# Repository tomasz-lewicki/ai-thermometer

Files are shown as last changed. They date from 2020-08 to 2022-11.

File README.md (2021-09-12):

# AI Thermometer
Contactless temperature mesurement using IR & RGB cameras and Deep CNN facial detection.

### Normal temperature

### Elevated temperature


## What's new in v0.4
* New facial detector (handles partial occlusion, e.g. with a mask)
* Added IR camera drift compensation with an external blackbody

## Hardware 
To build this project you will need:
|#|Part|link|Price (USD)|
|-|-|-|-|
|1|Jetson Nano Dev Kit|[link](https://www.sparkfun.com/products/16271)| 99 | 
|3|FLIR Lepton 3.5 IR Camera | [link](https://store.groupgets.com/products/flir-lepton-3-5)| 199 |
|4|GroupGets Purethermal2 Module | [link](https://store.groupgets.com/products/purethermal-2)| 99 |
|2|Raspberry Pi Camera Module V2.1 |[link](https://www.sparkfun.com/products/14028) | 25 |
|5|Noctua cooling fan | [link](https://www.amazon.com/Noctua-NF-A4x10-PWM-4-Pin-Premium/dp/B07DXRNYNX/) | 14 |
|6|3D printed enclosure | [https://a360.co/3nmDML3](https://a360.co/3nmDML3) | - |
|total | | | 436 |

Enclosure (live model available from [https://a360.co/3nmDML3](https://a360.co/3nmDML3) ): 
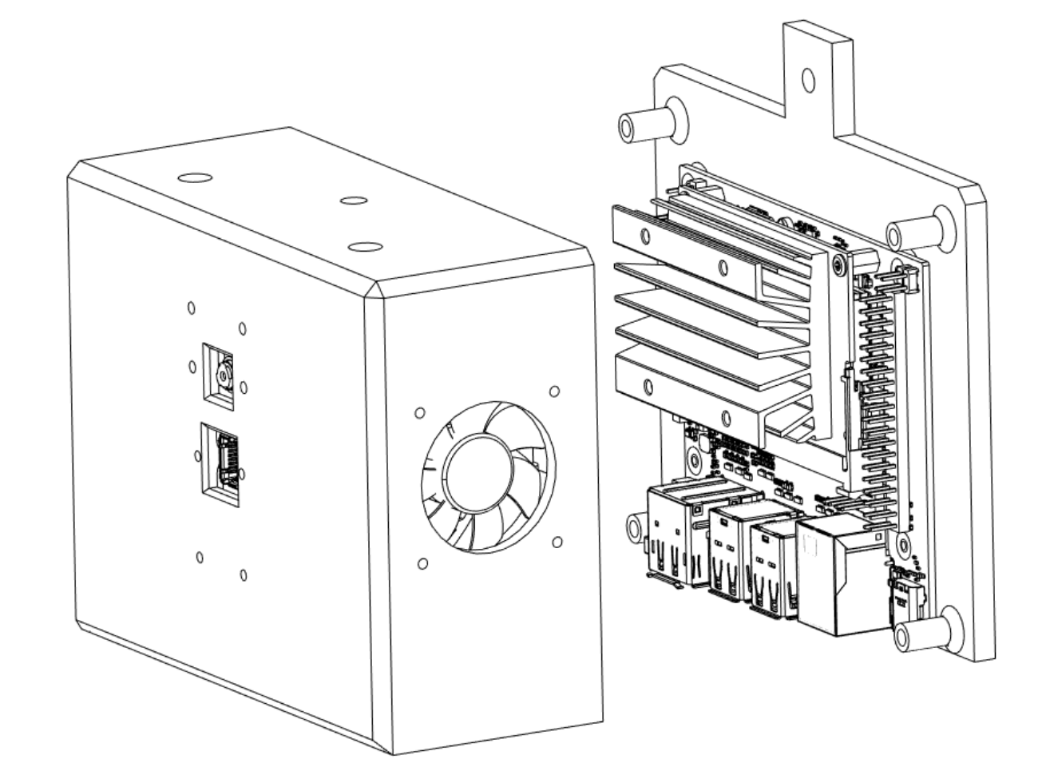
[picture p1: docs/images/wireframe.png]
wireframe image


## Quickstart 

1. Flash Nvidia Jetson Nano with the latest Nvidia JetPack. Update package manager

```shell
sudo apt update && sudo apt upgrade
```

2. Build OpenCV >4.4. It is required for CUDA DNN support.
```shell
wget https://raw.githubusercontent.com/mdegans/nano_build_opencv/master/build_opencv.sh
chmod +x build_opencv.sh
./build_opencv.sh
```
3. Build pytorch (instructions [here](https://forums.developer.nvidia.com/t/pytorch-for-jetson-version-1-7-0-now-available/72048))

4. Download AI Thermometer

```shell
git clone --recursive https://github.com/tomek-l/ai-thermometer
cd ai-thermometer
```

5. Run AI Thermometer

```shell
python3 main.py
```

6. Optionally, 3D print & assemble the enclosure from [https://a360.co/3nmDML3](https://a360.co/3nmDML3)

## Limitations

### IR and RGB camera alignment.

The current way of calculating the correspondence between IR and RGB cameras is not ideal.
Factors, such as the non-rigid mount of the sensor on the Raspberry Pi CMV2.1 don't help.
I'm actively working on calibration code that takes into account the intrinsic parameters of both cameras, which should allow for obtaining a pixel-level correspondence between the imags.

## FAQ/common issues:

1. `uvc_open error -3`

Reason: Your current user does not have r/w access to the PureThermal USB device. 

For a quick and dirty fix you can do do:
```shell
echo 'SUBSYSTEM=="usb",  ENV{DEVTYPE}=="usb_device", GROUP="plugdev", MODE="0664"' | sudo tee /etc/udev/rules.d/10-libuvc.rules 
sudo udevadm trigger
```
(this gives camera access to all users)

For a better, fine-grained permission setup, create a new group, give permissions to that group only and your user to the newly created group. You can read more [here](http://wiki.ros.org/libuvc_camera#Permissions).

2. `Illegal instruction (core dumped)`

Reason: The provided  ```libuvc.so``` is compiled for AArch64.
It is a custom version of libuvc that supports Y16 video format. If you're using different architecture, you will need to build the library from source:

```shell
git clone https://github.com/groupgets/libuvc
cd libuvc
mkdir build
cd build
cmake ..
make
cp libuvc.so ~/ai-thermometer/ir/libuvc_wrapper
```

3. using sudo or getting `permission denied`

You don't need ```sudo``` to run the code in this repository 🙂

## Previous versions

## Version 0.2: Haar Cascade + FLIR Lepton 3.5 temp. measurement (~10FPS, CPU only)
Watch full video: [https://www.youtube.com/watch?v=j9eo9Cs8J8I](https://www.youtube.com/watch?v=j9eo9Cs8J8I)

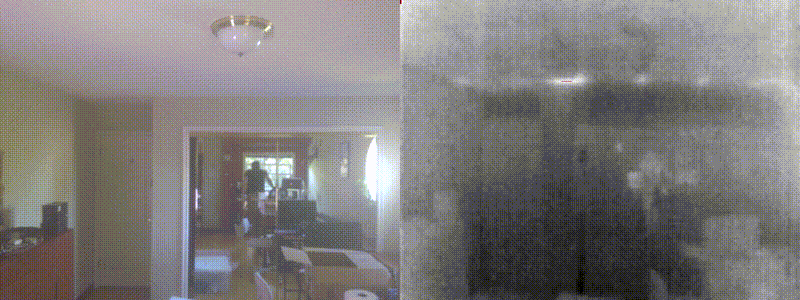
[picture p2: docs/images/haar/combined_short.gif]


## Version 0.1: SSD (COCO) + FLIR Lepton 3.5 temp. measurement (~12FPS w/ GPU accel.)
Watch full video: [https://www.youtube.com/watch?v=i2XMtshdjn8](https://www.youtube.com/watch?v=i2XMtshdjn8)



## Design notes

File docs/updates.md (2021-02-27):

# Hardware V2 update

## Camera Upgrade
The RGB camera module has been upgraded from the `Raspberry Pi CM V2.1` to a `Sainsmart IMX219`. 

The main reason for that change is the ridgidity of the assembly.
Specifically, the sensor on the CM V2.1 is held in place on the PCB with a piece of double-sided adhesive.
Even a sub-milimeter shift to the camera position can tilt the camera plane by a few degrees, and mess up the calibration.
That's bad for any machine-vision application.

In the Sainsmart camera module, the sensor is soldered to the PCB, and the plastic lens assembly is screwed down to the board. This is a much more ridgid assembly, making the RGB-IR alignment more robust.

## Antennas

# Software Update
- Support multiple detectors (SSD, retinaface)

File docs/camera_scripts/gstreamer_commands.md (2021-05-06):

# IR + RGB display simultaneously
```
gst-launch-1.0 nvarguscamerasrc sensor_mode=0 ! 'video/x-raw(memory:NVMM),width=3264, height=2464, framerate=21/1, format=NV12' ! nvvidconv flip-method=2 ! 'video/x-raw,width=800, height=600' ! videoconvert ! ximagesink & gst-launch-1.0 v4l2src device=/dev/video1 ! video/x-raw,format=UYVY ! videoscale ! video/x-raw,width=800,height=600 ! videoconvert ! ximagesink
```

# RGB

## Capture at full resolution, display on the screen
```shell
gst-launch-1.0 nvarguscamerasrc sensor_id=0 ! 'video/x-raw(memory:NVMM),width=3264, height=2464, framerate=21/1, format=NV12' ! nvvidconv flip-method=2 ! 'video/x-raw,width=960, height=720' ! nvvidconv ! nvegltransform ! nveglglessink -e
```

## Cropped
```shell
gst-launch-1.0 nvarguscamerasrc sensor_id=0 ! 'video/x-raw(memory:NVMM),width=3264, height=2464, framerate=21/1, format=NV12' ! nvvidconv flip-method=2 ! videocrop top=96 left=137 right=137 bottom=96 ! 'video/x-raw,width=800, height=600' ! nvvidconv ! nvegltransform ! nveglglessink -e
```

## General form to add cropping:
```
gst-launch-1.0 -v videotestsrc ! videocrop top=96 left=160 right=160 bottom=96 ! ximagesink
```

## Nvidia overlay display
```
gst-launch-1.0 nvarguscamerasrc sensor_mode=0 ! 'video/x-raw(memory:NVMM),width=3264, height=2464, framerate=21/1, format=NV12' ! nvvidconv flip-method=2  ! nvvidconv top=100 bottom=2364 left=300 right=3164 ! 'video/x-raw(memory:NVMM),width=1440, height=1080' ! nvoverlaysink display-id=0 -e
```

## take away 137 on the sides, 

horizontal: 3264-137=3127
vertical: 2464-96=2368
```
gst-launch-1.0 nvarguscamerasrc sensor_mode=0 ! 'video/x-raw(memory:NVMM),width=3264, height=2464, framerate=21/1, format=NV12' ! nvvidconv flip-method=2  ! nvvidconv top=96 bottom=2368 left=137 right=3127 ! 'video/x-raw(memory:NVMM),width=1440, height=1080' ! omxh264enc ! qtmux ! filesink location=RGB.mp4 -e 
```

## Saving to files
Save 1080p (sensor sub-frame)
```shell
gst-launch-1.0 nvarguscamerasrc ! 'video/x-raw(memory:NVMM), width=1920, height=1080,format=NV12, framerate=30/1'  ! nvvidconv flip-method=2 ! omxh264enc ! qtmux ! filesink location=1080p_output_cropped.mp4 -e
```

Save 1080p (from full frame, then resize)
```shell
gst-launch-1.0 nvarguscamerasrc sensor_mode=0 ! 'video/x-raw(memory:NVMM),width=3264, height=2464, framerate=21/1, format=NV12' ! nvvidconv flip-method=2 ! 'video/x-raw,width=1440, height=1080' ! omxh264enc ! qtmux ! filesink location=1080p_from_full.mp4 -e
```

--------------------------------------------------------------------------------------------------------------------------------------------------------

# Capture from IR Lepton Camera

## IR camera display (w/ colormap)
```shell
gst-launch-1.0 v4l2src device=/dev/video1 ! video/x-raw,format=UYVY ! videoscale ! video/x-raw,width=800,height=600 ! videoconvert ! ximagesink
```

## IR camera display (RAW 16bit values)
```shell
gst-launch-1.0 v4l2src device=/dev/video1 ! video/x-raw,format=GRAY16_LE ! videoscale ! video/x-raw,width=800,height=600 ! videoconvert ! ximagesink
```

## IR  - Save 

### Colormap to jpeg
```
gst-launch-1.0 v4l2src device=/dev/video1 num-buffers=1 ! video/x-raw,format=UYVY ! videoscale ! video/x-raw,width=800,height=600 ! nvjpegenc ! filesink location=test_ir.jpg
```

### Gray 16-bit 160x120 to mp4
```shell
gst-launch-1.0 v4l2src device=/dev/video1 ! video/x-raw,format=GRAY16_LE ! videoscale ! video/x-raw,width=160,height=120 ! videoconvert ! omxh264enc ! qtmux ! filesink location=grayscale_raw.mp4 -e
```
## Save to avi
gst-launch-1.0 v4l2src device=/dev/video1 ! video/x-raw,format=GRAY16_LE ! videoscale ! video/x-raw,width=800,height=600 ! videoconvert ! jpegenc ! avimux ! filesink location=test.avi -e

## Gray 8-bit resized to 800x600
gst-launch-1.0 v4l2src device=/dev/video1 ! video/x-raw,format=GRAY8 ! videoscale ! video/x-raw,width=800,height=600 ! videoconvert ! omxh264enc ! qtmux ! filesink location=grayscale_raw.mp4 -e

To record footage from both IR and RGB cameras at the same time, do:
```shell
bash deploy_rgb.sh & bash deploy_ir.sh ; fg
```

To combine the footage, do:
```shell
bash combine_ir_rgb.sh
```

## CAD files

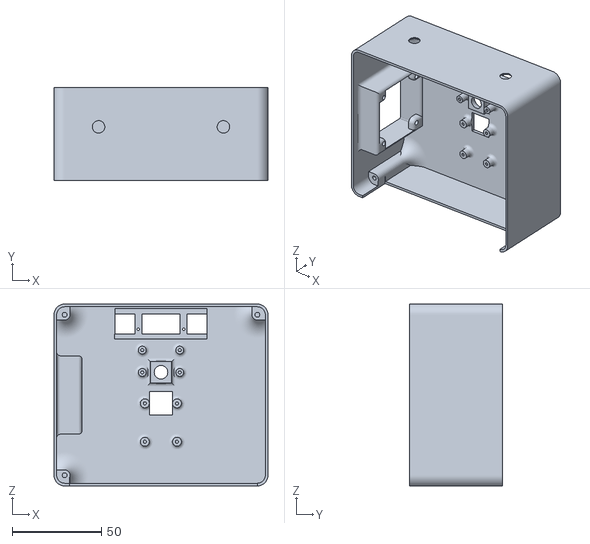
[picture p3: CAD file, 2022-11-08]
stl/top_shell.stl
120.0 x 52.0 x 102.0

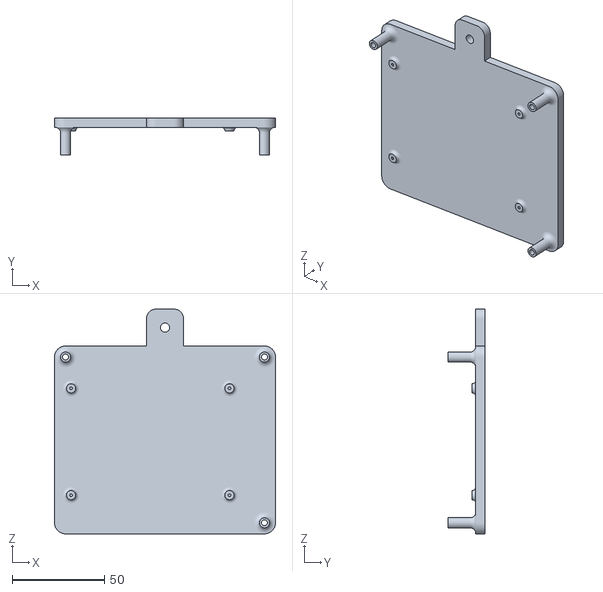
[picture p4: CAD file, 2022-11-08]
stl/base_plate.stl
120.0 x 20.0 x 122.0

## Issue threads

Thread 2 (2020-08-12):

tomasz-lewicki/ai-thermometer #2: where is requirements.txt

jazz-ai, 2020-08-12:
need requirements.txt

tomek-l, 2020-08-12:
Hi @jazz-ai !

The ```pip3 install -r requirements.txt``` was leftover from the previous AI Thermometer version that depended on ROS, as well as some other libraries. I will delete that line from the instructions.

Current version has no external requirements other than OpenCV 4.4  and nvidia Jetpack 4.4.

Let me know if you have any other issues.

jazz-ai, 2020-08-14:
I tried to run main.py
It is showing 
**uvc_open error -3**
and unable to start anything

tomek-l, 2020-08-16:
It means that your user doesn't have r/w access to the USB ports, so it cannot access the Pure Thermal device.

junartho, 2020-08-26:
hi @tomek-l 
nice codes. please tell me how to handle r/w access on usb ports.

tomek-l, 2020-08-26:
Hi @junartho 

If you want a quick and dirty solution do:
```shell
echo 'SUBSYSTEM=="usb",  ENV{DEVTYPE}=="usb_device", GROUP="plugdev", MODE="0664"' | sudo tee /etc/udev/rules.d/10-libuvc.rules 
sudo udevadm trigger
```
(this gives camera access to all users)

For a better, fine-grained permission setup, create a new group, give permissions to that group only and your user to the newly created group. You can read more [here](http://wiki.ros.org/libuvc_camera#Permissions).

tomek-l, 2020-08-26:
Let me know if that solved the problem :slightly_smiling_face:

junartho, 2020-08-26:
thank you for very fast response. 👍

closed 2020-08-26 by tomek-l

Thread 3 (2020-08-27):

tomasz-lewicki/ai-thermometer #3: Version 0.1: SSD (COCO) + FLIR Lepton 3.5 temp. measurement (~12FPS w/ GPU accel.)

junartho, 2020-08-27:
hi @tomek-l 

First of all, i wanna thank you for your codes. it really helps the communities at my place in this pandemic situation. however, these codes could only measure temperature with face straight to the camera and no mask used. i wonder if you have codes version 0.1 with SSD detection. I would appreciate it if you want to upload it.

tomek-l, 2020-08-28:
Hi @junartho ,

I didn't keep track of all the versions in parallel (v0.1, v0.2 and v0.3) but instead just overriding the repository with a newer version.  
You can view the v0.1 here: [https://github.com/tomek-l/ai-thermometer/tree/3bc78c2d7ce71a5f8fc7564c0c246c59196bae4e](https://github.com/tomek-l/ai-thermometer/tree/3bc78c2d7ce71a5f8fc7564c0c246c59196bae4e)

Keep in mind that the version 0.1:
1. Uses an SSD model, which is trained on the COCO dataset. While it gives you more classes (91 classes), it doesn't contain a "face" class, but rather a "person" class. This is less useful for the temperature estimation.

2. It uses ROS2 for communication. I dropped this approach in favour of communicating between threads. ROS2 is a bit of an overkill for this project, and folks might be unfamiliar with it. 

3. The setup is more involved, and the README is not as thorough.

I'm happy to help if you have any issues getting the v0.1 to work.

tomek-l, 2020-09-01:
Closing for now, but feel free to reopen if you have any further questions.

closed 2020-09-01 by tomek-l

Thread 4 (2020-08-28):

tomasz-lewicki/ai-thermometer #4: I am implementing ai thermometer with your kind explanation.

kos8108, 2020-08-28:
I am implementing ai thermometer with your kind explanation. 

Now I am building the environment of Raspberry pi camera v2 & lepton2.5 & PureThermal2.

But nothing has happened since Uvc_open error -3 appeared after python3 main.py. 

Can I know the solution? 

Of course, the individual operation of each sensor was confirmed.

thank you.

tomek-l, 2020-08-28:
Hi,

Did you change the permissions for the USB camera? (There's a short
explanation in readme.md)

kos8108, 2020-08-28:
Thank you so much.

It was executed with sudo without any problems.

Additionally, the temperature value of the ir sensor cannot be output, which part should I check?

Thank you always for your answer.

tomek-l, 2020-08-28:
Hey,

So if you wish to read the temperature value, you will need to add
something like this to the main loop:

print(ir_thread.frame.mean())

This will print the mean temperature of the 120x160 pixel array.

If you want to access the temperature of individual pixels, you'd do:

print(ir_thread.frame[0][0])

This way you'll access the value of the (0,0) pixel in degrees Celsius.

Hope this helps!

tomek-l, 2020-09-01:
Closing for now, but feel free to reopen if you have any further questions!

closed 2020-09-01 by tomek-l

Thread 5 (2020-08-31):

tomasz-lewicki/ai-thermometer #5: Couldn't get correct temperature

weshao, 2020-08-31:
Hi, I'm using Lepton 3.5 and purethermal 2, but my result temperature is around 100 (it should be close to 37,right?), and when I use the notebook(https://github.com/tomek-l/ai-thermometer/blob/master/docs/notebooks/Getting%20Started%20with%20Cameras.ipynb), the raw data for each pixel is around 8000 and after Kelvin to Celsius the result is around -195.
Do you have any idea about this?  Thanks.

tomek-l, 2020-08-31:
That's very weird. For me the raw values are (e.g. ~30315 for room at ~30deg C). The values being in 8000 range imply that the data is indeed in GRAY16_LE 16-bit format.

1. I presume that the following:
```shell
!gst-launch-1.0 v4l2src device=/dev/video1 ! video/x-raw,format=GRAY16_LE ! videoconvert ! ximagesink
```
gives you very dark (near black) image?

2. Could you send me an example png file from ```get_ir_image()``` so I can take a look?

You can use the following command to save a file:
```shell
!gst-launch-1.0 v4l2src device=/dev/video1 num-buffers=1 ! video/x-raw,format=GRAY16_LE ! videoconvert ! pngenc ! filesink location=/tmp/ir.png
```
It should be in ```/tmp/ir.png```

3. You are using jetson nano, right? Which version of jetpack?  What's the output of the following command?
```shell
gst-inspect-1.0 pngenc
```

weshao, 2020-09-01:
@tomek-l Thanks for the reply.
This is the running image:
[image]

1. the image is not very dark, it's gray.
[image]

2.The image
[image]

3. Yes, I'm using Jetpack 4.4 for Jetson Nano.
The output is:

```
Factory Details:
  Rank                     primary (256)
  Long-name                PNG image encoder
  Klass                    Codec/Encoder/Image
  Description              Encode a video frame to a .png image
  Author                   Jeremy SIMON <jsimon13@yahoo.fr>

Plugin Details:
  Name                     png
  Description              PNG plugin library
  Filename                 /usr/lib/aarch64-linux-gnu/gstreamer-1.0/libgstpng.so
  Version                  1.14.5
  License                  LGPL
  Source module            gst-plugins-good
  Source release date      2019-05-29
  Binary package           GStreamer Good Plugins (Ubuntu)
  Origin URL               https://launchpad.net/distros/ubuntu/+source/gst-plugins-good1.0

GObject
 +----GInitiallyUnowned
       +----GstObject
             +----GstElement
                   +----GstVideoEncoder
                         +----GstPngEnc

Implemented Interfaces:
  GstPreset

Pad Templates:
  SINK template: 'sink'
    Availability: Always
    Capabilities:
      video/x-raw
                 format: { (string)RGBA, (string)RGB, (string)GRAY8, (string)GRAY16_BE }
                  width: [ 1, 2147483647 ]
                 height: [ 1, 2147483647 ]
              framerate: [ 0/1, 2147483647/1 ]
  
  SRC template: 'src'
    Availability: Always
    Capabilities:
      image/png
                  width: [ 16, 1000000 ]
                 height: [ 16, 1000000 ]
              framerate: [ 0/1, 2147483647/1 ]

Element has no clocking capabilities.
Element has no URI handling capabilities.

Pads:
  SINK: 'sink'
    Pad Template: 'sink'
  SRC: 'src'
    Pad Template: 'src'

Element Properties:
  name                : The name of the object
                        flags: readable, writable
                        String. Default: "pngenc0"
  parent              : The parent of the object
                        flags: readable, writable
                        Object of type "GstObject"
  qos                 : Handle Quality-of-Service events from downstream
                        flags: readable, writable
                        Boolean. Default: false
  snapshot            : Send EOS after encoding a frame, useful for snapshots
                        flags: readable, writable
                        Boolean. Default: false
  compression-level   : PNG compression level
                        flags: readable, writable
                        Unsigned Integer. Range: 0 - 9 Default: 6 

```

tomek-l, 2020-09-09:
Hi @weshao 
Sorry it took me so long to get back to you! I couldn't figure it out, but I ran into a similar issue tonight on different hardware.

You're likely trying to use [Lepton 3.0](https://www.digikey.com/product-detail/en/flir-lepton/500-0726-01/500-0726-01-ND/6163867) (S/N: 500-0726-01), instead of [Lepton 3.5](https://www.digikey.com/product-detail/en/flir-lepton/500-0771-01/500-0771-01-ND/7606616) (S/N: 500-0771-01) module. 
They look the same and it's easy to get them confused. 

Unfortunately, Lepton 3.0 doesn't support radiometry, which is required to obtain the temperature values.

weshao, 2020-09-11:
Hi @tomek-l
Yes, you are right, I checked and found that I am using Lepton 3.0. 
Thank you for your answer :)

closed 2020-09-11 by weshao

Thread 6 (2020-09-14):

tomasz-lewicki/ai-thermometer #6: Running with web cam and IR cam, not accurate temperature reading

nickjrz, 2020-09-14:
Hi,

First of all, thanks for sharing the source code for this project, very helpful. I have been trying to run this code with a web cam instead of using the raspberry pi cam. I have it working with display and face detection, the only issue I am running into is that the temperature readings are not accurate. Would you have any idea what could be causing this behavior?

tomek-l, 2020-09-15:
Hi @nickjrz ,

Commit 9d754093d3fcf76fe9ce421dad255f20c7e582ec introduced a bug which led to incorrect readings. I just pushed 097c9c904fc412f0e25225afdf44eb3ec60b2f82 which fixed that. Let me know if the readings are better now :slightly_smiling_face:

nickjrz, 2020-09-15:
Thanks for your quick reply, I will try it today and will keep you updated.

nickjrz, 2020-09-15:
So I updated the files and I am still getting readings of 62550 celsius. I found a formula for the lepton thermal cameras temp  = slope * (raw -8192) + ambTemp  `https://groups.google.com/g/flir-lepton/c/T2NFRkeMyR4?pli=1` maybe this could be used along the calculations on code

tomek-l, 2020-09-15:
Hi,

Is it possible that you're using [Lepton 3.0](https://www.digikey.com/product-detail/en/flir-lepton/500-0726-01/500-0726-01-ND/6163867) (S/N: 500-0726-01), instead of [Lepton 3.5](https://www.digikey.com/product-detail/en/flir-lepton/500-0771-01/500-0771-01-ND/7606616) (S/N: 500-0771-01) module?

nickjrz, 2020-09-15:
So I have the lepton 3.0 and 2.0, as of now I am using the 2.0 model. I think I only need to add some calibration coefficient in the calculation in order for it to get readings properly.

tomek-l, 2020-09-15:
In order to get the temperature values out-of-the-box you'd have to have one of the **radiometric** lepton modules (e.g. Lepton 3.5). They come pre-calibrated and stream temperature values in Kelvin.

nickjrz, 2020-09-15:
Okay thanks, I guess I just need to figure out how to calibrate it. I tried ordering the 3.5 one but they were out of stock and only had 2.0 so I will keep you updated if I make any progress on this model.

nanogear, 2020-09-25:
@nickjrz try to buy the lepton directly to Groupgets or Digikey. Both have the radiometric 3.5 in stock

muralikrishna416, 2020-10-06:
Hai, i want to know small information like without IR Thermal sensor, the camera will open or will not open through the code which you have provided.

tomek-l, 2020-10-06:
Without the Lepton camera, the program will just indefinitely wait for IR
frames and display no output.

You can run just the RGB object detection with the script here:
https://www.github.com/tomek-l/ai-thermometer/tree/master/vis%2Fssd%2Fexample_detect_face_caffe_resnet.py

nickjrz, 2020-10-07:
I am currently waiting for a lepton 3.5 (digikey) to come in, as of now I am still trying to get the 3.0 to work with this application with some sort of calibration.

nickjrz, 2020-10-08:
I just got the lepton 3.5 and tried it out altogether but readings seem to be a little off. I am getting an average temperature of 32 Celsius. Do I need to let it run for a while for it to warm up?

tomek-l, 2021-02-27:
The freshly merged PR #31 adds:
- An option for adding an external blackbody reference
- Reports the average + maximal + 90th percentile temperature of the face, not just a single value.

You should pull the newest master give it a try :slightly_smiling_face:

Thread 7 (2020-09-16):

tomasz-lewicki/ai-thermometer #7: where can i get thermal from ur file

ROK-KJ, 2020-09-16:
i want get a putext and thermal(degree) information ur file..
but i cannot find it
please help me ;)

tomek-l, 2020-09-16:
Hi @ROK-KJ ,

Would you like a sample image file (e.g. in png format) from thermal camera?
Not sure if I understood correctly :)

ROK-KJ, 2020-11-09:
hello again.
main.py is for Version 0.3: ResNet-10 Facial Detection + FLIR Lepton 3.5 temp. measurement (~17 FPS w/ GPU accel.)??
i want to know how did you run this face detect by jetson GPU.

tomek-l, 2021-02-27:
Hi @ROK-KJ ,
Sorry to take a while to respond. The current version which supports:
* SSD with ResNet-10 backbone (see code [here](https://github.com/tomek-l/retinaface/tree/5f1f892d80a44a01f46b03ce767ce03417050ae5) )
* RetinaNet with Mobilenet backbone (see code [here](https://github.com/tomek-l/retinaface/tree/5f1f892d80a44a01f46b03ce767ce03417050ae5) )

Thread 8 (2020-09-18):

tomasz-lewicki/ai-thermometer #8: Incorrect Temperature values

jazz-ai, 2020-09-18:
It always shows human body temperature around 32-34 degree Celsius but actual temperature is always around 36-37 degree. How can I get accurate values? Are you using any calibration of Lepton 3.5 camera?

tomek-l, 2020-09-18:
Hi @jazz-ai 

1) What lens are you using? You're probably using a different field of view, hence the mismatch. I plan to update the code with support for different FOVs sometime.
2) Keep in mind that we're measuring the average skin surface temperature, which will be significantly lower (~33-36 deg C) than body core temperature (36-37 deg C).

razilla, 2020-11-16:
is there a way to calibrate the difference manually im have the same temperature issue (90.0 def F) the lens i am using is flir 3.5

nanogear, 2020-12-16:
I am having the same issue... @jazz-ai do you solved the issue?

tomek-l, 2021-02-27:
1. PR #31 adds an optional external blackbody measurement. That improves the accuracy dramatically.
2. Now I display much more comprehensive info about the facial temperature (avg+max+90th percentile), not just a single number.
3. There was briefly a camera calibration bug, which might have caused temperature readouts from the incorrect area in the image (fixed in e2fc37707c8f44a0c80dae196fccdb94971e0f23)

Anyway, one or more of those should solve the issue :smile:

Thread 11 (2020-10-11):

tomasz-lewicki/ai-thermometer #11: UVC error

razilla, 2020-10-11:
Hey Tomasz

Thanks for putting this out for people its a really cool project bro. I'm having trouble finding the video; I get the following error. Any idea trouble where I messed up? I'm thinking it may be how cameras are lined up. I 3d printed the case you gave but I noticed its slightly different than what you showed in the blog post. I attached a picture of how it look on my end was hoping if you thought that was maybe the problem. Also I 3d printed an Iron Man Helmet as a case I think you would appreciate. I attached that as well.

Thanks again,
Raza

[image]
[image]
[image]

 /ai-thermometer$ python3 main.py
Loading weights from file...
Weights loaded!
Running first net inference...
Detector initialized!
GST_ARGUS: Creating output stream
CONSUMER: Waiting until producer is connected...
GST_ARGUS: Available Sensor modes :
GST_ARGUS: 3264 x 2464 FR = 21.000000 fps Duration = 47619048 ; Analog Gain range min 1.000000, max 10.625000; Exposure Range min 13000, max 683709000;

GST_ARGUS: 3264 x 1848 FR = 28.000001 fps Duration = 35714284 ; Analog Gain range min 1.000000, max 10.625000; Exposure Range min 13000, max 683709000;

GST_ARGUS: 1920 x 1080 FR = 29.999999 fps Duration = 33333334 ; Analog Gain range min 1.000000, max 10.625000; Exposure Range min 13000, max 683709000;

GST_ARGUS: 1280 x 720 FR = 59.999999 fps Duration = 16666667 ; Analog Gain range min 1.000000, max 10.625000; Exposure Range min 13000, max 683709000;

GST_ARGUS: 1280 x 720 FR = 120.000005 fps Duration = 8333333 ; Analog Gain range min 1.000000, max 10.625000; Exposure Range min 13000, max 683709000;

GST_ARGUS: Running with following settings:
   Camera index = 0
   Camera mode  = 0
   Output Stream W = 3264 H = 2464
   seconds to Run    = 0
   Frame Rate = 21.000000
GST_ARGUS: Setup Complete, Starting captures for 0 seconds
GST_ARGUS: Starting repeat capture requests.
CONSUMER: Producer has connected; continuing.
[ WARN:0] global /tmp/build_opencv/opencv/modules/videoio/src/cap_gstreamer.cpp (935) open OpenCV | GStreamer warning: Cannot query video position: status=0, value=-1, duration=-1
uvc_open error -3

glbt, 2020-10-12:
This is permissions on the camera I believe, try it with sudo and see if it works :)

razilla, 2020-10-12:
Not getting the frames

raza@raza-desktop:~/ai-thermometer$ sudo python3 main.py
Loading weights from file...
Weights loaded!
Running first net inference...
Detector initialized!
GST_ARGUS: Creating output stream
CONSUMER: Waiting until producer is connected...
GST_ARGUS: Available Sensor modes :
GST_ARGUS: 3264 x 2464 FR = 21.000000 fps Duration = 47619048 ; Analog Gain rang                                                                          e min 1.000000, max 10.625000; Exposure Range min 13000, max 683709000;

GST_ARGUS: 3264 x 1848 FR = 28.000001 fps Duration = 35714284 ; Analog Gain rang                                                                          e min 1.000000, max 10.625000; Exposure Range min 13000, max 683709000;

GST_ARGUS: 1920 x 1080 FR = 29.999999 fps Duration = 33333334 ; Analog Gain rang                                                                          e min 1.000000, max 10.625000; Exposure Range min 13000, max 683709000;

GST_ARGUS: 1280 x 720 FR = 59.999999 fps Duration = 16666667 ; Analog Gain range                                                                           min 1.000000, max 10.625000; Exposure Range min 13000, max 683709000;

GST_ARGUS: 1280 x 720 FR = 120.000005 fps Duration = 8333333 ; Analog Gain range                                                                           min 1.000000, max 10.625000; Exposure Range min 13000, max 683709000;

GST_ARGUS: Running with following settings:
   Camera index = 0
   Camera mode  = 0
   Output Stream W = 3264 H = 2464
   seconds to Run    = 0
   Frame Rate = 21.000000
GST_ARGUS: Setup Complete, Starting captures for 0 seconds
GST_ARGUS: Starting repeat capture requests.
CONSUMER: Producer has connected; continuing.
[ WARN:0] global /tmp/build_opencv/opencv/modules/videoio/src/cap_gstreamer.cpp                                                                           (935) open OpenCV | GStreamer warning: Cannot query video position: status=0, va                                                                          lue=-1, duration=-1
device opened!
Version gpp: 0.0.0 dsp: 0.0.0
FLIR part #: b'\x00\x00\x00\x00\x00\x00\x00\x00\x00\x00\x00\x00\x00\x00\x00\x00\                                                                          x00\x00\x00\x00\x00\x00\x00\x00\x00\x00\x00\x00\x00\x00\x00\x00'
FLIR serial #: b'\x00\x00\x00\x00\x00\x00\x00\x00'
format: b'UYVY'
  frame 80x60 @ 9fps
format: b'Y16 '
  frame 80x60 @ 9fps
  frame 80x63 @ 9fps
format: b'Y8  '
  frame 80x60 @ 9fps
format: b'RGBP'
  frame 80x60 @ 9fps
format: b'}\xeb6\xe4'
  frame 80x60 @ 9fps
Estimated / selected altsetting bandwith : 13 / 642.
No protocol specified
Unable to init server: Could not connect: Connection refused

(python3:8113): Gtk-WARNING **: 11:53:00.221: cannot open display: :0
CONSUMER: Done Success
WARN: no frame
WARN: no frame
WARN: no frame
WARN: no frame
WARN: no frame
WARN: no frame
WARN: no frame
WARN: no frame
WARN: no frame
WARN: no frame
WARN: no frame
WARNING Argus: 5 client objects still exist during shutdown:
        547884820536 (0x7f04003b88)
        547891253568 (0x7f040018c0)
        547891253728 (0x7f04001960)
        547891258416 (0x7f04001ac0)
        547891259712 (0x7f04003a70)

tomek-l, 2020-10-14:
Hi @razilla !

As @glbt  said, It looks like an issue with r/w permissions for the USB device.

I posted a solution in [readme](https://github.com/tomek-l/ai-thermometer#make-sure-your-user-has-rw-access-to-the-camera-device) under  "Common Issues"

If you do the following, you should be able to run this code without `sudo`.
```shell
echo 'SUBSYSTEM=="usb",  ENV{DEVTYPE}=="usb_device", GROUP="plugdev", MODE="0664"' | sudo tee /etc/udev/rules.d/10-libuvc.rules 
sudo udevadm trigger
```
Let me know if the other issue persists with the new udev rules & without sudo :slightly_smiling_face:

tomek-l, 2020-10-14:
If you refer to the post on hackster.io, I posted it a while back and probably updated the enclosure design since then :) 
Also, cool mask! :smile:

deantheiceman, 2020-10-19:
Hi @tomek-l reallly nice work. I have the same problem, getting 

```
waiting for rgb frames
Warn: no frame
```
I also tried running as root still got the same problem

Any suggestions?

tomek-l, 2020-10-19:
Hi @deantheiceman !

Looks like the gstreamer pipeline got initialized correctly, but we're not getting any RGB frames upon `.read()`.

This can occur if something crashes on `nvargus` side. Most of the time restarting it should solve the problem:
```
sudo systemctl restart nvargus-daemon
```

Let me know if this helped! :slightly_smiling_face:

deantheiceman, 2020-10-20:
Hi @tomek-l thanks for the reply. I tried rebooting and also restarting the service with no luck, 

```
CONSUMER: Producer has connected; continuing.
[ WARN:0] global /tmp/build_opencv/opencv/modules/videoio/src/cap_gstreamer.cpp (935) open OpenCV | GStreamer warning: Cannot query video position: status=0, value=-1, duration=-1
uvc_open error -3
```

Although the error message seems to be slightly different

nanogear, 2020-10-26:
> Hey Tomasz
>
> Thanks for putting this out for people its a really cool project bro. I'm having trouble finding the video; I get the following error. Any idea trouble where I messed up? I'm thinking it [...]

So, just to get this clear...the position of the cameras as Razilla have them are ok to work with?

razilla, 2020-10-29:
@nanogear 
Yes the positions work where I put them. You should see two different screens when you get it running so the positioning can vary slightly is what I've noticed.
The  screens actually seem to operate independently from one another. i.e. you can have two people in infrared and only one in the RGB or vice versa but you really have to be trying to do that.

[image]

closed 2020-10-29 by razilla

nanogear, 2020-11-12:
> Hi @tomek-l thanks for the reply. I tried rebooting and also restarting the service with no luck,
> 
> ```
> CONSUMER: Producer has connected; continuing.
> [ WARN:0] global /tmp/build_opencv/opencv/modules/videoio/src/cap_gstreamer.cpp (935) open OpenCV | GStreamer warning: Cannot query video position: status=0, value=-1, duration=-1
> uvc_open error -3
> ```
> 
> Although the error message seems to be slightly different
> 
> _EDIT_: Got it working, thanks so much

Can you explain me how you fix it please? 

When applying the "dirty solution" I get:  ENV{DEVTYPE}=="usb_device,: command not found

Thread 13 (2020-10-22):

tomasz-lewicki/ai-thermometer #13: Interface for deployment

deantheiceman, 2020-10-22:
Hi,

Thanks so much for your work this is really interesting. 

I was wondering what kind of interface have you used for actual deployment. I saw you were working on a web interface, does that work? For us to put on a screen near the camera display?

Would be nice to have like an audio alert which we could play maybe through the web interface if someone is detected above the desired range.

Also curious if you're using the flir 3.5 as well, do you need any calibration? My detection seems to be a little bit off

Thanks again

tomek-l, 2021-01-14:
Hi @deantheiceman ! Sorry for getting to you so late.
1. I currently use a regular HDMI output & a simple window OpenCV based interface under X-server.
2. I did work on a http-based interface a while back (see b6711bc30a28c0b60db8c1ea6a334ba20b582e1b), but never merged it to master. 

Do you have any suggestions w.r.t how the interface should be realized?

tomek-l, 2021-01-14:
As far as the second part of your question goes:
Te IR camera has an inherent temperature drift that will affect the readings. That's why I plan to implement calibration with an external blackbody reference in an upcoming version of the software.
I set up issue #24 to hear suggestions on how this should be realized, feel free to comment :slightly_smiling_face:

deantheiceman, 2021-01-16:
hi @tomek-l thanks for the reply.

Something like what they show here would be really useful https://www.tintahijau.com/images/2019-2/001_Hikvision.jpg

We setup your project in our small office, we have a TV display people as they come in. But it'll be useful if we could track if someone goes above the threshold and then save that image and throws an alarm if they are above. In the other examples they track a picture of each unique person that came in.

Thanks again for the great work. Really wish I could help

deantheiceman, 2021-01-16:
Another nice way commercial projects have implemented it is like this 
[image]

So the logic is like:

- if face detected
- if below temp show green lights with the temp
- if above take picture, throw alarm

Maybe we can do it with the http interface, but my pthon skills are really bad :(

deantheiceman, 2021-01-31:
Hi @tomek-l sorry to bump this, do you think you will merge the web interface into master?

tomek-l, 2021-02-03:
Hi! 

Let me give a little bit of background on that.
I'm looking for something that would fulfill the following 4 criteria:
* no issues in major browsers
* low enough latency (2s maximum)
* decent framerate (~5FPS at minimum)
* streaming to multiple clients without impeding the performance of the main app. (at least 3 devices)

The closest I got to that goal was by simply streaming a jpeg sequence to the browser. 
That's available on the `http_streaming` branch (b6711bc) and works out perfectly for a single device.

Unfortunately, the per-client memory footprint is high, and I'm unable to handle >2 clients without impact on the main app.
I'm looking for a better solution, and dragging my feet on merging that to master for that reason.

tomek-l, 2021-02-03:
You know @deantheiceman, now that I think about it more, I was streaming a full `768x1024px` frame to the browser. 
Maybe I should give it a try with something smaller and see what happens.

deantheiceman, 2021-02-08:
Thanks, happy to test if you get anything going. I noticed the screenshot rules also really impact performance, disabling that got me much better performance. Would be useful if we could snapshot when they trigger the increased temperature

tomek-l, 2021-02-27:
Hi @deantheiceman !

Feel free the newest version. It has new and improved interface.

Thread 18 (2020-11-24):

tomasz-lewicki/ai-thermometer #18: (NOT AN ISSUE) Neopixel to indicate "fever" in a detection

nanogear, 2020-11-24:
I am trying to use Neopixels on this project,. Recently Adafruit coded some libraries for the Neopixels that are useful in the Jetson Nano using CircuitPython. It works pretty nice...

I want to make the Neopixel stay ON with green colour when the Jetson Nano be in fever screening mode and when a 37.5 C temperature is detected, the Neopixel changes the colour to red for example... I need some help to incorporate it to the Tomasz project.

Here a simple tutorial to make Neopixels work with the Jetson Nano:

Install Pip3 if not already installed:
`sudo apt-get install python3-pip`

Reboot

Install Adafruit-Blinka 5.8.0:
`pip3 install Adafruit-Blinka`

Enable SPI on Jetson Nano:
`sudo /opt/nvidia/jetson-io/jetson-io.py`

- Select Configure 40-pin expansion header at the bottom.

- Select spi1 (19, 21, 23, 24, 26) and then select Back 

- Finally select Save and reboot to reconfigure pins. This will create a config file and reboot the Jetson Nano.

After the Nano boots up again, verify you have the I2C devices with the command:
`ls /dev/i2c* /dev/spi*`

You can test to see what I2C addresses are connected by running `sudo i2cdetect -r -y 0` (on pins 27/28) or `sudo  i2cdetect -r -y 1` (on pins 3/5)

Then, we need to set user permissions. In order to use the Jetson GPIO Library, the correct user permissions/groups must be set first. Start by creating a new gpio user group:

`sudo groupadd -f -r gpio`
`sudo usermod -a -G gpio pi`

Clone the Repo and copy the rules:

`cd ~`
`git clone https://github.com/NVIDIA/jetson-gpio.git`
`sudo cp ~/jetson-gpio/lib/python/Jetson/GPIO/99-gpio.rules /etc/udev/rules.d`

_This section was originally written for releases before JetPack 4.3. For JetPack 4.3, the udev rules are in: /lib/udev/rulesd/60-jetson-gpio-common.rules. This should mean that you don’t have to copy the file anymore with JetPack 4.3 and above._ 

 _Also, it appears as if the default is for users to be included in the gpio group. You can check this by:_
`$ groups`

Reboot

Update just in case if a library is missing:
`sudo pip3 install --upgrade adafruit_blinka`

Install  CircuitPython NeoPixel_SPI library;:

`pip3 install adafruit-circuitpython-neopixel-spi`

Reboot again and that´s all!!!

Connect "Din" of your Neopixel to the SPI1_MOSI pin of your Jetson Nano(pin 19 of the expansion header), Gnd to Gnd and 5v to 5v.

try this example:

`import board`
`import neopixel_spi`

`pixels = neopixel_spi.NeoPixel_SPI(board.SPI(), 10)`
`pixels.fill(0xff0000)` 

You can check the Hex colors to use whatever colour you want by using this web page:
[https://www.color-hex.com/](url)
-------------------------------------------------------------------------------------------------------------------

tomek-l, 2020-11-24:
Hi @nanogear !

Neat idea! I thought about it a little bit before, but never implemented it :slightly_smiling_face:
The only way of controlling neopixels I knew about was by using a bit-banged protocol for the ws2812, but that required 100% of one CPU core, so I gave up on this. Looks like `NeoPixel_SPI` library lets you use `SPI` hardware, without hogging the CPU :+1: 

Let me take a look at the library and get back to you! :slightly_smiling_face:

tomek-l, 2021-02-23:
Started working on this feature in c7983eada39b24c398912b355df1523b5348e0e2 (see [image]).

Will add modified 3D printed enclosure that supports neopixels soon.

nanogear, 2021-02-26:
Awesome Tomasz, thank you very much for your kind work!!

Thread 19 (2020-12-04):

tomasz-lewicki/ai-thermometer #19: White box on RGB Camera out of sync with IR Camera

aaronf99, 2020-12-04:
Hello,
I have copied your project directly, using the same casing. After running the program, I can see that the frame of reference is off. Is there a fix for this?
[image]
[image]
[image]
[image]

tomek-l, 2021-01-14:
Hi there, @aaronf99 !

Yup, that's a bug. I was experimenting with a different RGB camera with a wider FOV and merged code to master, but the publicly available hardware for that is not yet updated. In the future, the system will support multiple cameras with different FOVs. I will probably also start a "stable" branch to avoid issues like that in the future.

aaronf99, 2021-01-14:
Thanks for the reply @tomek-l 

That makes sense, I am using the Raspberry Pi Camera Module V2.
Is there a quick fix I can do for this as the area that I currently work in could really do with this right now.

Many Thanks,
Aaron

tomek-l, 2021-01-24:
Hi @aaronf99!

e2fc37707c8f44a0c80dae196fccdb94971e0f23 introduces a hotfix for this bug. Checkout the newest master, and let me know if that looks better. 

The alignment could still be a bit off at a distance. The reason is the way the sensor is attached to Raspberry Pi CM V2.1 PCB (double sided tape). Due to that the RGB sensor will be mounted at a slightly different angle in different units (that's why I'm experimenting with a different cameras in the first place). I will also work out support for cameras with different FOVs in a future version.

closed 2021-01-27 by aaronf99

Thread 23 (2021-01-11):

tomasz-lewicki/ai-thermometer #23: Calibrating Lepton 3.5 for Outdoor vs Indoor

rgpettit, 2021-01-11:
Has anyone run into calibration issues when using this outdoors - particularly in winter?  The system works perfectly inside with ambient temperatures of 66-72F.  However, trying to use it outdoors <45F produces really drastic readings on the facial detections - typically over 1000F!

I've tried leaving the system outside but am still having the same problems.  I'm a track & field coach and am trying to set this up to screen athletes so I need it to work outside.  Any suggestions would be greatly appreciated.

Thanks!

rgpettit, 2021-01-13:
UPDATE -  it's not the cold temperatures but rather sunlight that seem to be the problem.  Works perfectly in my cold garage but as soon as it's in the sun, reading go crazy.  It's not even facing the sun directly - just the presence of sunlight affects it.

nanogear, 2021-01-13:
Probably this is your problem... emissivity:

https://www.flir.eu/discover/professional-tools/how-does-emissivity-affect-thermal-imaging/

tomek-l, 2021-01-14:
Hi @rgpettit !

That's a really great application and I hope that I can be of help :slightly_smiling_face: 

Lepton 3.5 is capable of sensing up to 150C in low-gain mode, and 450C in high-gain mode.
It's therefore not capable of producing a (valid) reading reading of 537C (1000F), so I doubt that it's an environmental factor.
The bug is likely caused by:
- a bug on my side in processing
- you're running a different version of lepton hardware than I do

1. Would you be able to share some visuals illustrating the problem? Could be a screenshot of the AI Themometer UI, or the output of this `gstreamer` command: `gst-launch-1.0 v4l2src device=/dev/video1 ! video/x-raw,format=UYVY ! videoscale ! video/x-raw,width=800,height=600 ! videoconvert ! ximagesink`
2. Could you confirm which lepton version are you running (3.0, 3.5, radiometric/non-radiometric)?

rgpettit, 2021-01-14:
Thanks so much for your help!  I am using the radiometric Lepton 3.5 from DigiKey.  Images attached from both the UI and gstreamer.  "Normal" images were taken in front of a windowed door with full sun in the background.  "Sun" images were taken standing in the same spot but with that door open.  I get the same "normal" results anywhere indoors and the same "sun" results anywhere outside during the day.

Hope this makes sense.  As you might notice from the UI image, I'm working with one-arm after injuring myself in T&F :-)

[image]
[image]
[image]
[image]

nanogear, 2021-01-14:
Hello,

Hope everybody is doing well. I tried to do the same today. Put the system in front of an open window(seeing the exterior light but not directly to the sun) and I am having the same results as @rgpettit 

I am using the Flir Lepton 3.5(radiometric). Indoor works pretty good.

[image]

nanogear, 2021-01-23:
@rgpettit Hi, have you found a solution to the issue? Regards

rgpettit, 2021-01-23:
Nothing yet, but I haven't had much time to look into it the last week or so.  @tomek-l, have you discovered anything either?

tomek-l, 2021-01-24:
Hi there! 

I was able to reproduce the bug. It was due to uint16 type underflow during conversion from Kelvin to Celsius, and
328b29349f4f3e57665feb9bb87b527504821fd4 should fix this. 
I knew that Lepton 3.5 has (-10C to 400C) range, but I never really tested that -10C to 0C part of it in California :slightly_smiling_face: 
Checkout the newest `master` branch, and it should work!

rgpettit, 2021-01-24:
Excellent!  Great find - works perfectly for me now.  Thanks!

closed 2021-01-24 by rgpettit

nanogear, 2021-01-25:
It worked for me too. Thank you very much!!!!

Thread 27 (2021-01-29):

tomasz-lewicki/ai-thermometer #27: Adding support for SPI lepton board: let me know what you think!

tomek-l, 2021-01-29:
I'm leaning towards using SPI directly (rather than USB) for interfacing Lepton 3.5 in a future hardware revision.

* It would bring down the cost of the device (the GroupGets Purethermal board costs ~100USD).
* It would mitigate the need for bulky USB connectors inside the case.
* The transition should be relatively easy. The [pylepton](https://github.com/groupgets/pylepton) package could be used to interface lepton module.

If you're using AI Thermometer and have any thoughts on this change, feel free to comment below.

CristinaPosada, 2021-02-16:
Hi! This would be very interesting! 
I do not have the Purethermal, I have the breakoutboard V2 and I would like to use ai-thermometer

123Dante123, 2021-04-02:
Hey Tomasz, are you still planning to add support for the SPI lepton board?

Skylakc, 2024-07-16:
Hello Tomasz! Are u still developing the SPI feature?

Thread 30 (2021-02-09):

tomasz-lewicki/ai-thermometer #30: Camera connection?

Thanh-Binh, 2021-02-09:
thanks for sharing us your work.
I understood that you use NVidia Nano Dev Kit with 2 cameras: Visible and Lepton 3.5.
Could you please share me information which visible camera you use and how to connect all camera with Nano? via MIPI-CS2 or SPI?
Thanks

tomek-l, 2021-02-27:
Hi @Thanh-Binh ! 

I use:
- Raspberry Pi Camera Module V2.1 connected via MIPI-CSI2
- Lepton 3.5 connected via PureThermal2 usb board

A while ago I wrote a [post](https://www.hackster.io/tomasz-lewicki/ai-thermometer-2bacb4) you might find helpful.

Thanh-Binh, 2021-02-27:
Hi Atomen
Thanks for your response!
1. I do not know about Jetson Nano. How can you compile and run opencv face and eye detection on it?

2. how can you calculate body core Temperatur based on face skin temperature?

3. do you plan to use DNN to detect face and facial landmarks directly from thermal images?

Thanks 

Gesendet mit der mobilen Mail App

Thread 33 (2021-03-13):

tomasz-lewicki/ai-thermometer #33: Error occur in ai-thermometer!! Please Guide me to resolve this problem

Henery1, 2021-03-13:
File "main.py", line 13, in <module>
    from rgb import RGBThread
  File "/home/thermal/ai-thermometer/rgb/__init__.py", line 1, in <module>
    from .rgb_thread import *
  File "/home/thermal/ai-thermometer/rgb/rgb_thread.py", line 8, in <module>
    from .retinaface import RetinaFaceDetector
  File "/home/thermal/ai-thermometer/rgb/retinaface/__init__.py", line 1, in <module>
    from .detector import *
  File "/home/thermal/ai-thermometer/rgb/retinaface/detector.py", line 10, in <module>
    from .models.retinaface import RetinaFace
  File "/home/thermal/ai-thermometer/rgb/retinaface/models/retinaface.py", line 5, in <module>
    import torchvision.models.detection.backbone_utils as backbone_utils
ModuleNotFoundError: No module named 'torchvision.models.detection'

tomek-l, 2021-03-13:
Hi @Henery1 

This looks like a mismatch between `torchvision` versions.
It was likely caused by an issue in installation instructions.
I'll look into this!

tomek-l, 2021-03-13:
@Henery1 

What version of `torch` and `torchvision` are you using?
You can check that by inspecting the output of the following commands:

```bash
pip3 show torchvision
pip3 show torch
```

Henery1, 2021-03-16:
Hi Tomek ! First of all Thanks you very much for your kindly respond. I used for thermal-view with purethermal-2 break out board and FLIR Lepton 3.5 and RGB for pi-camera v-2.1. Please Look at the torch and torchvision below:
For Torch 
Name: torch
Version: 1.8.0
Summary: Tensors and Dynamic neural networks in Python with strong GPU acceleration
Home-page: https://pytorch.org/
Author: PyTorch Team
Author-email: packages@pytorch.org
License: BSD-3
Location: /home/thermal/.local/lib/python3.6/site-packages
Requires: numpy, dataclasses, typing-extensions

For Torchvision
Name: torchvision
Version: 0.2.2.post3
Summary: image and video datasets and models for torch deep learning
Home-page: https://github.com/pytorch/vision
Author: PyTorch Core Team
Author-email: soumith@pytorch.org
License: BSD
Location: /home/thermal/.local/lib/python3.6/site-packages
Requires: six, pillow, numpy, torch

                                                                                                yours sincerely
                                                                                                         Henery T

Henery1, 2021-03-16:
Hi @tomek-l !! May I know Do you have an (ai-thermometer.img) file? If you have that kind of clone .img file Please share me or show me where i can download it. I tried many times and got the errors because of my few programming knowledge. Thanks a lot
                                                                                                      Yours sincerely
                                                                                                      Henery T

Henery1, 2021-03-18:
Hi @tomek-l <https://github.com/tomek-l> ! First of all Thanks you very
much for your kindly respond. I used for thermal-view with purethermal-2
break out board and FLIR Lepton 3.5 and pi-camera v-2.1 for RGB . Please
Look at the torch and torchvision below:
For Torch
Name: torch
Version: 1.8.0
Summary: Tensors and Dynamic neural networks in Python with strong GPU
acceleration
Home-page: https://pytorch.org/
Author: PyTorch Team
Author-email: ***@***.***
License: BSD-3
Location: /home/thermal/.local/lib/python3.6/site-packages
Requires: numpy, dataclasses, typing-extensions

For Torchvision
Name: torchvision
Version: 0.2.2.post3
Summary: image and video datasets and models for torch deep learning
Home-page: https://github.com/pytorch/vision
Author: PyTorch Core Team
Author-email: ***@***.***
License: BSD
Location: /home/thermal/.local/lib/python3.6/site-packages
Requires: six, pillow, numpy, torch

                     yours sincerely

                              Henery T

Henery1, 2021-03-18:
Hi @tomek-l <https://github.com/tomek-l> !! May I know Do you have an
(ai-thermometer.img) file? If you have that kind of clone .img file Please
share me or show me where i can download it. I tried many times and got the
errors because of my few programming knowledge. Thanks a lot
Yours sincerely
Henery T

Henery1, 2021-03-18:
PLease help me to get the ai-thermometer .img file. I really need your
project .img files . Please as soon as possible to share your ai
thermometer .img file. Thanks a lot

Henery1, 2021-03-22:
Hi @tomek-l 
I got that kind of error. Please guide me to get RGB and IR frame display.

(488) isPipelinePlaying OpenCV | GStreamer warning: unable to query pipeline state
[ WARN:1] global /tmp/build_opencv/opencv/modules/videoio/src/cap_gstreamer.cpp (1761) handleMessage OpenCV | GStreamer warning: Embedded video playback halted; module nvarguscamerasrc0 reported: TIMEOUT
GST_ARGUS: Cleaning up
Exception in thread Thread-1:
Traceback (most recent call last):
  File "/usr/lib/python3.6/threading.py", line 916, in _bootstrap_inner
    self.run()
  File "/home/thermal/ai-thermometer/rgb/rgb_thread.py", line 38, in run
    frame_small = cv2.resize(self._frame, (400, 300))
cv2.error: OpenCV(4.4.0) /tmp/build_opencv/opencv/modules/imgproc/src/resize.cpp:3929: error: (-215:Assertion failed) !ssize.empty() in function 'resize'

(960, 0)
Waiting for RGB frames
Waiting for RGB frames
Waiting for RGB frames
Waiting for RGB frames
Waiting for RGB frames
Waiting for RGB frames

tomek-l, 2021-03-22:
Hi @Henery1 ,
I'm glad you were able push it forward. Te second error is likely related to the gstreamer pipeline for RGB camera not having set up successfully. 

1. See if you can display camera 0 on the screen:
```shell
gst-launch-1.0 nvarguscamerasrc sensor_id=0 ! 'video/x-raw(memory:NVMM),width=3264, height=2464, framerate=21/1, format=NV12' ! nvvidconv flip-method=2 ! 'video/x-raw,width=960, height=720' ! nvvidconv ! nvegltransform ! nveglglessink -e
```
(or camera 1):
```shell 
gst-launch-1.0 nvarguscamerasrc sensor_id=1 ! 'video/x-raw(memory:NVMM),width=3264, height=2464, framerate=21/1, format=NV12' ! nvvidconv flip-method=2 ! 'video/x-raw,width=960, height=720' ! nvvidconv ! nvegltransform ! nveglglessink -e
```

2. If these commands don't succeed, give this a try:
```
sudo systemctl restart nvargus-daemon
```

Henery1, 2021-03-23:
Hi @tomek-l Everything is fine now and trying to upgrade to your program. At first I got an error in camera and tried to check the camera with this command ls /dev/video0. Anything have changed and got an error again, then try to install the video 4 linux utils with this command (sudo apt-get install v4l-utils) and then check video list (v4l2-ctl --list-devices). The output was fine. Thanks a lot for your kindly respond.

LXPWing, 2021-03-24:
Hi @Henery1 What version of torch , torchvision and python are you using? I'm having a problem with the version

Henery1, 2021-06-02:
Hi Tomek-I!!! I want to get the Tavg data. But I don't know how can i get this Tavg data in your program. Where can i find the data set in your program? Thanks a lot!!! Waiting for your kindly reply.

Henery1, 2021-06-02:
> 
> 
> Hi @Henery1 What version of torch , torchvision and python are you using? I'm having a problem with the version

I used Torch version 1.8.0 .

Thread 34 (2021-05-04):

tomasz-lewicki/ai-thermometer #34: Import Error make_imx219_capture

rtime2awaken, 2021-05-04:
I'm stepping through main.py with pdb and getting: ImportError: cannot import name 'make_imx219_capture' 
I'm hoping there is a simple fix.  It looks like it has to to with the Pi camera.  I also have the lepton 3.5.  Any advice
would be much appreciated.

tomek-l, 2021-05-06:
Hi @rtime2awaken !

This looks like the RGB frame didn't get grabbed correctly. Could you confirm that you're able to see camera output by doing either:

```shell
gst-launch-1.0 nvarguscamerasrc sensor_id=0 ! 'video/x-raw(memory:NVMM),width=3264, height=2464, framerate=21/1, format=NV12' ! nvvidconv flip-method=2 ! 'video/x-raw,width=960, height=720' ! nvvidconv ! nvegltransform ! nveglglessink -e
```

or 

```shell
gst-launch-1.0 nvarguscamerasrc sensor_id=1 ! 'video/x-raw(memory:NVMM),width=3264, height=2464, framerate=21/1, format=NV12' ! nvvidconv flip-method=2 ! 'video/x-raw,width=960, height=720' ! nvvidconv ! nvegltransform ! nveglglessink -e
```

Let me know if you can see anything on the screen.

rtime2awaken, 2021-05-06:
> Hi @rtime2awaken !
>
> This looks like the RGB frame didn't get grabbed correctly. Could you confirm that you're able to see camera output by doing either:
>
> ```shell
> gst-launch-1.0 nvarguscamerasrc [...]

It has been fixed!  I was using the v1 Pi camera that was causing the problem.  Thank you for getting back with me.  This is a great project.

closed 2021-05-06 by rtime2awaken

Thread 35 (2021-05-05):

tomasz-lewicki/ai-thermometer #35: Using an USB camera

jjferreira, 2021-05-05:
Hi there how can  make this code run using a usb camera, instead of the camera suggested in your article.

tomek-l, 2021-05-06:
Hi @jjferreira !

1) You're probably better off using CSI camera. Using a USB camera will need more CPU to copy data & decode the video stream from USB.
2) If you still want to use a USB camera here's how you'd do it:

Substitute [this line](https://github.com/tomek-l/jetson-cameras/blob/d8ff3729c9bd9d6eb06e9339aecbdc856878b2cf/__init__.py#L37) from
```python
cap = cv2.VideoCapture(gst_string, cv2.CAP_GSTREAMER)
```

to
```python
cap = cv2.VideoCapture('/dev/video3')
```

This assumes that your USB camera is on `/dev/video3`. If you don't know which device node the USB cam is associated with, do `dmesg -w` and observe the output while plugging the USB camera.

Hope this helps!

jjferreira, 2021-05-07:
Hi @tomek-l , thank you for this response, but I'm a bit confused.  This file u asked me to make a change its on a different project and repository.  I downloaded the **ai-thermometer** repository and the changes are on the **jetson-cameras** repository, do you mind clarifying.

Thank you

tomek-l, 2021-05-14:
Hi @jjferreira ,

What webcam are you using?
Did you have any success so far in getting the image in other applications?

jjferreira, 2021-05-14:
I tried my intel realsense d435i, and a standard logitech Usb camera.  Same
behaviour.  But if i run a simple python script i can see both cameras
working as expected.

Tks

jjferreira, 2021-06-28:
The issued I was having was to do with the lens of the thermal became loose.

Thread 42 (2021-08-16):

tomasz-lewicki/ai-thermometer #42: Camera Issue

BasilHarun, 2021-08-16:
[image]

can you help me with this erroor

tomek-l, 2021-08-16:
Hi there!

This should help :slightly_smiling_face: 
```shell
echo 'SUBSYSTEM=="usb",  ENV{DEVTYPE}=="usb_device", GROUP="plugdev", MODE="0664"' | sudo tee /etc/udev/rules.d/10-libuvc.rules 
sudo udevadm trigger
```

You can read more about this in the [FAQ](https://github.com/tomek-l/ai-thermometer/blob/master/README.md#faqcommon-issues)

BasilHarun, 2021-08-16:
Hi, 

Thanks for replying, I’ve tried it out but see everytime it gives different error 
resize error is due to it doesn't detect pi camera
and waiting for ir frames is due to empty pipline of ir thread

[image]

The only thing I think I’m using Nano 2Gb could it be because of the memory.

BasilHarun, 2021-08-16:
[image]
[image]

BasilHarun, 2021-08-16:
[image]

tomek-l, 2021-08-16:
Yeah, so those are two separate issues:
1) with Pi Camera 
2) with USB permissions for Lepton 3.

To try addressing 1)

I'd start by restarting argus:
```shell
sudo systemctl restart nvargus-daemon.service
```
After restart, try this:
```shell
gst-launch-1.0 nvarguscamerasrc ! 'video/x-raw(memory:NVMM),  width=(int)1920, height=(int)1080, format=(string)NV12,  framerate=(fraction)30/1' ! nvoverlaysink
```
Can you see video on the screen?

Regarding 2): are you still seeing `uvc_open error -3`?

BasilHarun, 2021-08-16:
Hi, 

I did all the steps accordingly, and can see the video. 

Then I ran Python3 Main.py, 

on side note (I had a low memory warning on right hand corner.)

this is the result. 

[image]

[image]

BasilHarun, 2021-08-17:
After fixing RGB Error, it gives me the IR error. 

[image]

BasilHarun, 2021-08-17:
Also I’m Using Jetson Nano 2GB not 4GB and when I run main.py it always gives me this error on side. 

[image]

BasilHarun, 2021-08-17:
When I run the IR camera individually, I get this empty error. 

[image]

closed 2021-08-18 by BasilHarun

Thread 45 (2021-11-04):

tomasz-lewicki/ai-thermometer #45: USB camera issue

immkapoor, 2021-11-04:
I am using a simple logitech usb camera with jetson xavier but I am getting a uvc_find_error error but the camera is getting detected and activated. Everything is working well with simple codes.

immkapoor, 2021-11-07:
Can you please provide me the dependencies for this repo? Which versions of opencv and pytorch are you using?

tomek-l, 2021-11-09:
Hi!

The uvc_error is likely due to the purethermal module not getting detected
(which is also a UVC device).

As far as the versioning goes:
- OpenCV> 4.4
- pytorch > 1.9

The latest releases of both should work.

immkapoor, 2021-11-09:
@tomek-l Thank you for responding. I am using a FLIR E75 camera along with legion usb camera. Both are getting detected by other codes but i am getting a device error while running this code. I am using opencv v4.4.0. I am getting warnings from gstreamer. Can you suggest anything? It'll be helpful. 
[image]
r

tomek-l, 2021-11-09:
Hi @immkapoor,

Here you would change:
https://github.com/tomek-l/ai-thermometer/blob/6be49fe3880a3381ed5b66a7fcbf8b74992ab476/rgb/rgb_thread.py#L24

To something like:
```python
self._stream = cv2.VideoCapture("/dev/video1")  
```
Where `/dev/video1` will be device handle to your USB webcam.

tomek-l, 2021-11-09:
I implemented this project with Raspberry Pi CM V2.1 which is a CSI _(Camera Serial Interface)_ camera, which has different API than your USB camera - that's why you're getting errors.

Keep in mind that when you get these two to work without errors, you will still have to make sure that the images from the two cameras "align". It's fairly simple for FLIR Lepton 3.5 and Rpi CM V2.1, because they have very similar field-of-view.

immkapoor, 2021-11-09:
@tomek-l I made the suggested changes. But I am still getting the same error. The usb camera is getting enabled but I am not able to see the camera's capture screen.  Do you think it's because of warnings raised by gstreamer
[image]
?

tomek-l, 2021-11-09:
That's odd. Did you remove the call to `make_imx219_capture()`?
That's the line of code that initializes gstreamer pipeline.

immkapoor, 2021-11-09:
@tomek-l No, i haven't made any changes in code. Just added legion camera in init.py and flir camera in rgb_thread

immkapoor, 2021-11-14:
@tomek-l Hey, I was able to solve the Gstreamer warning by replacing cv2.VIdeoCapture("/dev/video*") in cv2.VIdeoCapture("/dev/video", cv2.CAP_V4L2) and if I do make_imx_capture() then I get uvc device error and program terminates. If I replace that with another simple video capture then also I get ucv find device error but nothing comes on screen. Do you have any idea?

immkapoor, 2021-11-16:
@tomek-l I am not able to find the find device error in init code of libuvc wrapper. Can you please tell me where its definition is coming from?

tomek-l, 2021-11-16:
Hi @immkapoor 

These two are two separate methods of creating a camera device:
- `cv2.VIdeoCapture()` 
- `make_imx_capture()`

You have to choose just one. Since you are working with a USB camera, I recommend doing `cv2.VIdeoCapture("/dev/video0", cv2.CAP_V4L2)` and deleting the `make_imx_capture()` call.

tomek-l, 2021-11-16:
As far as the error codes go, you can look them up in [libuvc](https://github.com/groupgets/libuvc) source code.

Specifically, in [libuvc.h](https://github.com/groupgets/libuvc/blob/5e866910de3f172bd5adab72baec40a066bbbe3a/include/libuvc/libuvc.h#L23) you have definitions of what each error number means.

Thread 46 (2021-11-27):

tomasz-lewicki/ai-thermometer #46: Can't load an ONNX model in SSD Detector

rjv-vila, 2021-11-27:
I want to change the model used in SSD Detector with my custom trained model which is an onnx and it is an facemask detector. Is it possible to use my model to detect facemask and the temperature of the person? I have modified the detector.py in SSD folder into this to load the my model :
        parent_dir_pth = os.path.dirname(os.path.abspath(__file__))
        onnx_model_pth = (
            parent_dir_pth + "/caffe/ssd-mobilenet.onnx"
        )
        self._net = cv2.dnn.readNetFromONNX(onnx_model_pth)

but I get this error

Loading SSD weights from file...
Traceback (most recent call last):
  File "main.py", line 220, in <module>
    rgb_thread = RGBThread(model=FACE_DET_MODEL)
  File "/home/g1-facemask/ai-thermometer/rgb/rgb_thread.py", line 18, in __init__
    self._detector = SsdDetector()
  File "/home/g1-facemask/ai-thermometer/rgb/ssd/detector.py", line 18, in __init__
    self._net = cv2.dnn.readNetFromONNX(onnx_model_pth)
cv2.error: OpenCV(4.4.0) /tmp/build_opencv/opencv/modules/dnn/src/dnn.cpp:604: error: (-2:Unspecified error) Can't create layer "433" of type "Exp" in function 'getLayerInstance'

Is there a thing that I can do? 
Should I retrain my model that gets caffemodel and prototxt like the default? If yes, is there any tutorial to do that kind of training?

tomek-l, 2021-11-29:
Hi @rjv-vila ,

Exp layer was added in OpenCV 4.5.2. by this PR: https://github.com/opencv/opencv/pull/19545

You will need to upgrade from OpenCV 4.4. All AI Thermometer functionality should still work under OpenCV 4.5.2.

rjv-vila, 2021-11-29:
Thank you for your reply @tomek-l , should I upgrade it by building like in your instructions

wget https://raw.githubusercontent.com/mdegans/nano_build_opencv/master/build_opencv.sh
chmod +x build_opencv.sh
./build_opencv.sh

or pip install will do?

tomek-l, 2021-11-29:
You will need to build from source to have CUDA acceleration.

rjv-vila, 2021-11-29:
Alright, thanks again. I will edit the version of the opencv written in the build_opencv.sh then build it. Is it the proper way of doing that? I saw that the default version of opencv written in build_opencv.sh is 4.4.0 so I though I just need to edit it.

rjv-vila, 2021-11-29:
@tomek-l here is what I get after upgrading to OpenCV 4.5.2

`Loading SSD weights from file...
Weights loaded!
Running first net inference...
Detector initialized!
GST_ARGUS: Creating output stream
CONSUMER: Waiting until producer is connected...
GST_ARGUS: Available Sensor modes :
GST_ARGUS: 3264 x 2464 FR = 21.000000 fps Duration = 47619048 ; Analog Gain range min 1.000000, max 10.625000; Exposure Range min 13000, max 683709000;

GST_ARGUS: 3264 x 1848 FR = 28.000001 fps Duration = 35714284 ; Analog Gain range min 1.000000, max 10.625000; Exposure Range min 13000, max 683709000;

GST_ARGUS: 1920 x 1080 FR = 29.999999 fps Duration = 33333334 ; Analog Gain range min 1.000000, max 10.625000; Exposure Range min 13000, max 683709000;

GST_ARGUS: 1640 x 1232 FR = 29.999999 fps Duration = 33333334 ; Analog Gain range min 1.000000, max 10.625000; Exposure Range min 13000, max 683709000;

GST_ARGUS: 1280 x 720 FR = 59.999999 fps Duration = 16666667 ; Analog Gain range min 1.000000, max 10.625000; Exposure Range min 13000, max 683709000;

GST_ARGUS: 1280 x 720 FR = 120.000005 fps Duration = 8333333 ; Analog Gain range min 1.000000, max 10.625000; Exposure Range min 13000, max 683709000;

GST_ARGUS: Running with following settings:
   Camera index = 0 
   Camera mode  = 0 
   Output Stream W = 3264 H = 2464 
   seconds to Run    = 0 
   Frame Rate = 21.000000 
GST_ARGUS: Setup Complete, Starting captures for 0 seconds
GST_ARGUS: Starting repeat capture requests.
CONSUMER: Producer has connected; continuing.
[ WARN:0] global /tmp/build_opencv/opencv/modules/videoio/src/cap_gstreamer.cpp (1081) open OpenCV | GStreamer warning: Cannot query video position: status=0, value=-1, duration=-1
device opened!
Version gpp: 3.3.26 dsp: 3.3.26
FLIR part #: b'500-0771-01\x00\x00\x00\x00\x00\x00\x00\x00\x00\x00\x00\x00\x00\x00\x00\x00\x00\x00\x00\x00\x00'
FLIR serial #: b'\x02\xf1<\x01\x00\x00\x00\x00'
format: b'UYVY'
  frame 160x120 @ 9fps
format: b'Y16 '
  frame 160x120 @ 9fps
  frame 160x122 @ 9fps
format: b'Y8  '
  frame 160x120 @ 9fps
format: b'RGBP'
  frame 160x120 @ 9fps
format: b'}\xeb6\xe4'
  frame 160x120 @ 9fps
Estimated / selected altsetting bandwith : 18 / 642. 
INFO: Using $DISPLAY from environment, not from config
(960, 0)
Waiting for IR frames
exit handler called
releasing
GST_ARGUS: Cleaning up
CONSUMER: Done Success
GST_ARGUS: Done Success
Traceback (most recent call last):
  File "main.py", line 244, in <module>
    mainloop()
  File "main.py", line 142, in mainloop
    boxes_ir = transform_boxes(boxes, 1.1, 1.1, 0, 0)
  File "/home/g1-facemask/ai-thermometer/utils/transforms.py", line 49, in transform_boxes
    x1, y1, x2, y2 = bbox
ValueError: not enough values to unpack (expected 4, got 1)
`

tomek-l, 2021-12-01:
Hi @rjv-vila ! 

Your Neural Net likely has a different output format than the network I used, so the existing code won't work.
To make it work, you you'd have to parse the output of your neural network to extract the bounding boxes from the output tensor.

rjv-vila, 2021-12-01:
Hello @tomek-l thank you again for replying.

Do you have any idea on how to do that? I'm kinda clueless on how I will do that process.

closed 2022-01-20 by rjv-vila

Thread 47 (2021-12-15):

tomasz-lewicki/ai-thermometer #47: How to get started

geannealva, 2021-12-15:
Hi @tomek-l ! I hope you could help me.

I am a graduating college student. I have a thesis about face mask detection and body temperature detection.. I am currently working on my model for the mask detection, however I really do not know how to get started with the temperature detection. I also have the same idea which is to detect the inner eye canthus for temperature measurement, (using haar as well?). I am also planning to buy the same materials. But I really don't know how the code works or how I will calibrate the cameras. I am still a beginner in machine learning with python because I studied on my own. I hope you could help me, I really want to learn. This is the only project I found helpful. Thank you so much! 😅

rjv-vila, 2021-12-16:
@geannealva I think I can help you since we have the same project as I posted in Issue#46. You can send me an email.
Josebustamante2019@gmail.com

tomek-l, 2021-12-16:
Hi @geannealva !

As much as I'd love to help, I probably don't have the throughput to do that :slightly_smiling_face: 
If you have specific questions, feel free to ask them here.

tomek-l, 2021-12-16:
Referring to the question from the topic: "How to get started".

The starting point I'd recommend is to:

1. Buy the IR camera
2. Try running this script [pt2_example.py](https://github.com/tomek-l/ai-thermometer/blob/6be49fe3880a3381ed5b66a7fcbf8b74992ab476/ir/pt2_example.py#L106). At [Line 106](https://github.com/tomek-l/ai-thermometer/blob/6be49fe3880a3381ed5b66a7fcbf8b74992ab476/ir/pt2_example.py#L106) `temp_map` will be a numpy array in Celsius. Try measuring the temperature of objects in front of the IR camera.
3. Once you have IR and RGB cameras running, go to [Getting started with cameras](https://github.com/tomek-l/ai-thermometer/blob/master/docs/notebooks/Getting%20Started%20with%20Cameras.ipynb) notebook and try combining IR and RGB footage.

geannealva, 2021-12-16:
@rjv-vila thank you so much!

geannealva, 2021-12-16:
@tomek-l thank you so much!

rjv-vila, 2022-01-20:
@geannealva My email above was hacked. If you're from PH , you can contact me in anbuflame16@gmail.com

yagmurarsln0509, 2022-08-01:
Hello, need some advice please.. I run this script pt2_example.py. I measure the temperature of objects in front of the IR camera. But  I am getting syntax error when executing Getting started with cameras.ipynb example. 
!gst-launch-1.0 v4l2src device=/dev/video1 num-buffers=1 ! video/x-raw,format=GRAY16_LE ! videoconvert ! pngenc ! filesink location=/tmp/ir.png
ı run code in the shell. So I  remove the preceding '!' from the command.
gst-launch-1.0 v4l2src device=/dev/video1 num-buffers=1 ! video/x-raw,format=GRAY16_LE ! videoconvert ! pngenc ! filesink location=/tmp/ir.png
out : SyntaxError: invalid syntax
Please . Can you help me ?

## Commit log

2020-03-27 added gtreamer camera snippets
2020-03-27 added camera scripts
2020-04-04 renamed camera curses
2020-04-05 added prototype for rgb->ir coord transformation
2020-04-05 added concurrent temperature reading in obj. detection node
2020-04-11 added a script for capturing jpgs from both cameras
2020-04-12 added saving to jpgs and heatmaps
2020-06-24 renamed gstreamer_pipelines to camera_scripts
2020-06-24 temperature measurement running with haar
2020-07-19 moved camera_scripts
2020-08-02 added new version of main with better threading support
2020-08-02 working GPU thread
2020-08-02 IR + VIS threaded display working"
2020-08-02 threaded version working with upscaling and normalization, still problems with temp resolution
2020-08-05 purethermal printing demo working
2020-08-06 removed silly print
2020-08-06 added main thread and IR thread latency info
2020-08-06 added saving frames using ThreadPoolExecutor
2020-09-02 make the display example actually display stuff 🙃
2020-09-02 disabled saving frames by default
2020-09-09 added .temperatures property to ir thread
2020-09-09 updated v3.0 with temperature overlay
2020-09-16 decoupled FRAME_SIZE from WIN_SIZE
2020-09-16 added heatmaps
2020-11-18 added wireframe images
2021-01-19 Add retinaface and camera submodules
2021-01-19 Use cv2 capture object from cameras submodule
2021-01-21 Save both IR and RGB frames in the same directory
2021-01-21 Add frame zooming out
2021-01-21 Add combined view prototype
2021-01-24 Hotfix: adjust camera alignemnt params for RP CM v2.1
2021-02-08 Add temperature reading
2021-02-08 Report 3 different temperature readings in interface.py
2021-02-08 Make temperature() a regular function, and not property
2021-02-08 Add blackbody calibration option
2021-02-27 Remove FRAME_SIZE parameter from config
2021-02-27 Remove rouge debug prints from main.py
2021-02-27 Change default camera transormation parameters
2021-02-27 Override temperature array with calibration
2021-02-27 Remove debug coordinate print from interface.py
2021-03-08 Clean up calibration code
    -Create function that wraps calibration logic in main.py
    -Disable calib box in interface.py if calibration is disabled as calibration box can confuse users
2021-03-09 -Added logic to set calib_box=None if calibrate=false in config.py so we can pass less arguments to make_ir_view()
2022-11-08 Add 3D models
    [base_plate.stl, top_shell.stl]
